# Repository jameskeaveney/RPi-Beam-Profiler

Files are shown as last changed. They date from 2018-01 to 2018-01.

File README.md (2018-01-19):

Raspberry Pi Beam Profiler
==========================
**Version 1.0.0**

A platform for inexpensive automatic laser beam profiling for finding the focal position and beam width of a laser beam, using a commercial translation stage, stepper motor, raspberry pi computer and the Pi NoIR camera module.

This repository contains the electronics schematics, mechanical drawings, list of components and python codes to construct and run the Raspberry Pi Beam Profiler.

See the user guide PDF for detailed installation instructions.

The paper, currently available on the arxiv (arxiv.org/abs/...), details the operation and exemplifies some results from the beam profiler.

-----------------

**Revision History**

v1.0.0
- Initial commit

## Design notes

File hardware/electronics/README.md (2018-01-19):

These are the electronic design files for the RPi beam profiler. 

The design files use KiCAD (http://kicad-pcb.org/). The PCB designs can be uploaded in their current .kicad_pcb file format to oshpark.com for board manufacture. If gerber files are required, open the pcb file in KiCAD first and output gerber files from there.

The daughter board sits on top of the RPi GPIO pins, and includes:

> A high-current 5V voltage regulator to power the RPi
> The Pololu DRV8825 motor controller breakout board

This should be powered by a high current (> 2A) DC voltage supplied via the barrel connector (centre positive).

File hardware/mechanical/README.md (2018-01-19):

Mechanical drawings for the Raspberry Pi Beam Profiler.

Drawings are provided as pdf files and Autodesk inventor (2016 version) IPT files.

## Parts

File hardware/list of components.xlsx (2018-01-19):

Raspberry Pi Beam Profiler - list of component parts
Off-the-shelf components - mechanical
Item | Quantity | Supplier | Part Number / Order Code | Web link
Translation Stage | 1 | Thorlabs | PT1/M | https://www.thorlabs.com/thorproduct.cfm?partnumber=PT1/M
Post holder | 2 | Thorlabs | PH20/M
Posts (or longer depending on need) | 2 | Thorlabs | TR50/M
16mm cage rods (longer or shorter depending on need) | 2 | Thorlabs | SR4
Thumb-screw | 1 | Thorlabs | TS6H/M
Stepper motor - Nanotec ST4209S1006-B | 1 | Farnell | 4743143 | http://uk.farnell.com/nanotec/st4209s1006-b/stepper-motor-0-9deg-2-phase/dp/4743143?ost=Nanotec+ST4209S1006-B&iscrfnonsku=false
Flexible shaft coupling - Ruland MWS20-5-5-SS | 1 | RS | 325-8218 | https://uk.rs-online.com/web/p/flexible-beam-couplings/3258218/
M2.5 standoffs (8mm, but length not important) | 8
M2 standoffs (5mm length) | 4 |  | 500-6558 | https://uk.rs-online.com/web/p/threaded-standoffs/5006558/
M2.5x6mm screws | 8
M3x6mm screws | 13
M6x12mm socket-head cap screw | 2
M2x3mm set screw | 2
M2x4mm screws | 4
M2x8mm screws | 2
Custom components - mechanical
Base plate | 1
Motor holder | 1
Micro-switch holder | 1
Camera mount | 1
Camera filter mount - SM1 adapter | 1
Symmetric post-mounting piece | 1
Custom screw | 1
Screw housing | 1
Electronics mount | 1
Off the shelf components - electronics
Raspberry Pi Model 3 B | 1 | RS | 896-8660 | https://uk.rs-online.com/web/p/processor-microcontroller-development-kits/8968660/
Raspberry Pi NOIR Camera | 1 | RS | 913-2673 | https://uk.rs-online.com/web/p/video-modules/9132673/
Pololu DRV8825 Breakout board | 1 | Hobbytronics | DRV8825 | http://www.hobbytronics.co.uk/drv8825-stepper-motor-driver
0.1" Jumper wires | 6 | Hobbytronics | PRT-12796 | http://www.hobbytronics.co.uk/cables-connectors/jumper-wires/jumper-wires-ff-6in
DC Barrel Jack Power supply, 12V, 3A | 1 | RS | 903-2902 | https://uk.rs-online.com/web/p/plug-in-power-supply/9032902/
Micro-switch, DM1-02P-30-3 | 1 | Farnell | SW05202 | http://onecall.farnell.com/multicomp/dm1-02p-30-3/microswitch-spdt-1a-sim-lever/dp/SW05202?ost=SW05202
Custom components -electronics
Power and motor controller board | 1

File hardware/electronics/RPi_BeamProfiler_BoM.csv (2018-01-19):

Id | Designator | Package | Quantity | Designation | Supplier and ref
1 | C1,C3 | CP_Radial_D6.3mm_P2.50mm | 2 | 100uF
2 | C2 | CP_Radial_D10.0mm_P5.00mm | 1 | 1000uF
3 | CON1 | BARREL_JACK | 1 | BARREL_JACK
4 | D1 | D_5W_P5.08mm_Vertical_AnodeUp | 1 | 1N5822
5 | L1 | INDUCTOR_V | 1 | 100 uH
6 | SW1 | Pin_Header_Straight_1x02_Pitch2.54mm | 1 | SW_DIP_x01
7 | SW2 | SW_DIP_x1_W7.62mm_Slide_LowProfile | 1 | SW_DIP_x01
8 | U1 | TO-220-5_Pentawatt_Multiwatt-5_Vertical_StaggeredType1 | 1 | LM2576HVS-5
9 | U3 | DRV8825_BreakoutBoard | 1 | DRV8825BreakoutBoard
10 | U2 | Pin_Header_Straight_2x20_Pitch2.54mm | 1 | Raspberry_Pi_2_3
11 | P1 | Pin_Header_Straight_1x04_Pitch2.54mm | 1 | CONN_01X04
Plus additional 0.1" headers for attaching connecting the DRV8825 breakout board (e.g. http://www.hobbytronics.co.uk/cables-connectors/pcb-headers-sockets/36way-header-254)

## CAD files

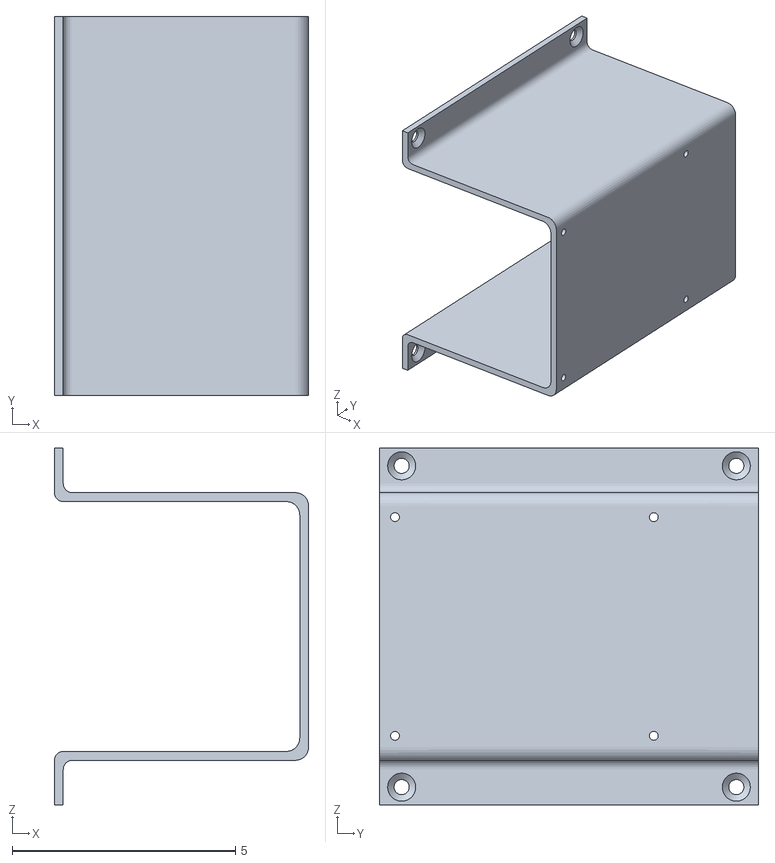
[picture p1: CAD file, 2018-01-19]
hardware/mechanical/drawings/electronics_mount_3dprint.stl
5.70 x 8.50 x 8.00

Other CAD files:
hardware/electronics/KiCAD files/RPi_BeamProfiler.kicad_pcb_Outline.ipt

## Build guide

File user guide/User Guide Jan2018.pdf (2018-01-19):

## Raspberry Pi Beam Profiler

## Users Guide

James Keaveney
james.keaveney@durham.ac.uk

Version 1.0.0

Last updated 2018/01/19

Contents

1. Introduction
2. Setting up the hardware
a. Stuff you will need
b. What goes where
3. Setting up the Raspberry Pi
4. Software Guide
a. Starting the software
b. The front panel
c. Live View
d. Camera settings
e. Translation stage scan settings
f. Export options
g. Image analysis method
h. Program Information
5. Hardware specifications

### 1. Introduction

The Raspberry Pi beam profiler is designed to be a replacement for knife-edging, particularly with one or two fixed-mount lenses where the focal point and size need to be known.

With a conventional knife-edging setup, this task is laborious and time-consuming. With this beam profiler, the idea is to completely automate the process.

It is also possible to perform M-squared measurements of beam quality or further analysis by outputting the raw image data.

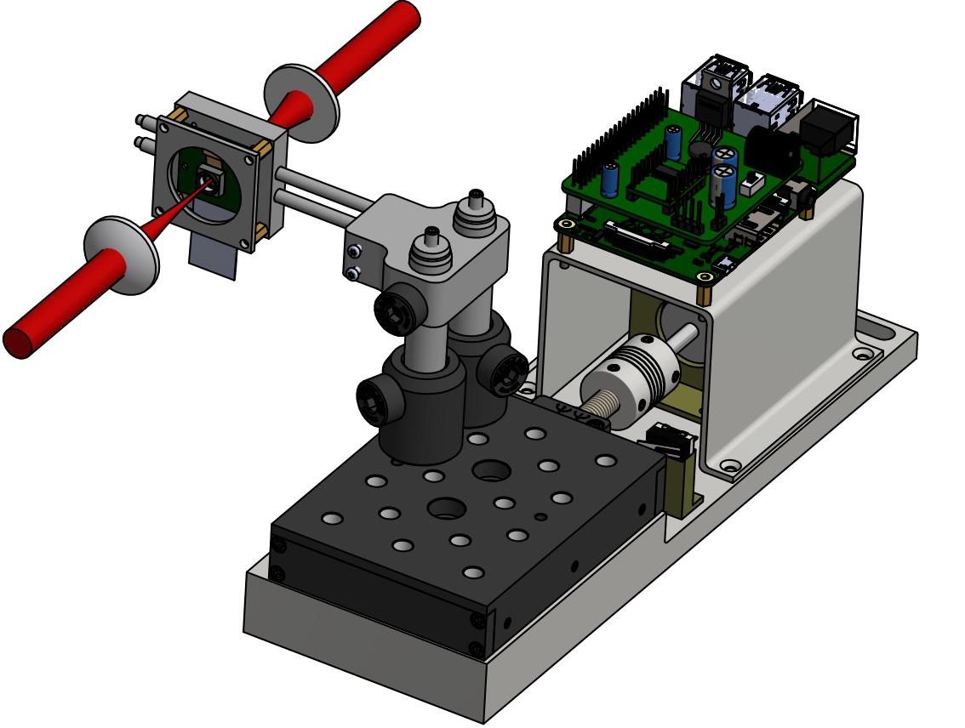
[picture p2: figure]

### 2. Setting up the hardware

a. What you will need:

In addition to the main beam profiler assembly, you will need the following parts:

- Raspberry Pi – we recommend the Model 3B version (or whichever is the latest), since it has by far the most processing power
- A micro-SD card with at least 8 GB capacity. We recommend getting a card with a fast read speed, which will maximise system performance.
- HDMI to HDMI / DVI cable, for connecting a monitor
- Monitor with either DVI or HDMI input. Recommended resolution of at least 1440 x 900.
- Keyboard and Mouse (both USB)
- USB memory stick for retrieving data
- DC power supply, with a barrel jack connector, capable of supplying 8-12 V with more than 2A to power the Raspberry Pi and stepper motor

The RPi’s local storage is a Micro-SD card. This should be installed, located near the bottom of the board, on the reverse side, as it stands in the beam profiler. We recommend using the Raspbian operating system (see section 3 below).

b. What goes where?

We recommend manufacturing the PCB designed for this purpose, in which case the PCB pushes on to the Raspberry Pi via the 2x20 GPIO header connection. However, it is not required, and the DRV8825 breakout board can be used by itself with only a few GPIO pin connections (note in this case the raspberry pi will have to be powered separately via the Micro-USB connector on the RPi board itself). For manually connecting the pins, the connection diagram is shown schematically below, along with the pin numbering scheme of the Raspberry Pi (Model B+, Model 2B, Model 3B).

CAUTION: Incorrect wiring could lead to short circuits which WILL damage the Raspberry Pi. Make sure it’s right before turning on, and never connect or disconnect anything while the Raspberry Pi is powered up.

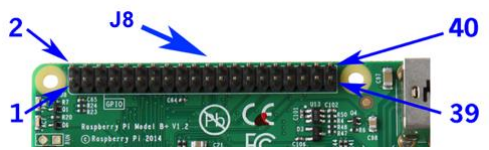
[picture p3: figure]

Figure 1: Raspberry Pi Model B+ GPIO Header pin numbering. The odd-numbered pins are along one side, and pin 2 is located nearest the edge of the RPi board. Image from http://pi4j.com/pins/model-b-plus.html

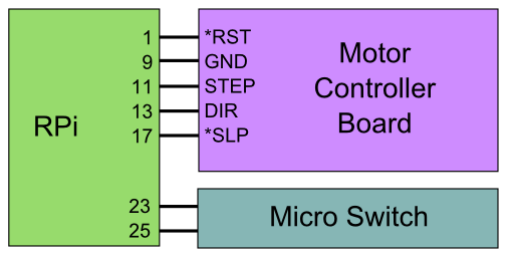
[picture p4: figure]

Figure 2: Connection diagram. Pin numbers on the RPi correspond to those in figure 1. The pins on the Motor controller are labelled accordingly.

Connect jumper wires between the pins of the RPi and Motor controller, as shown in figure 2. Connect the stepper motor via the A1,A2,B1,B2 pins of the motor controller board. Finally, connect the micro-switch to the RPi.

The motor controller is a Polou breakout board (product page here), (http://www.pololu.com/product/2133) consisting of a DRV8825 chip (datasheet is here). (http://www.pololu.com/file/download/drv8825.pdf?file_id=0J590) This is capable of driving up to 2.2A per coil. The current is actively controlled, and a potentiometer controls the current limit. If a different stepper motor is used, this current limit can be reset for the new motor (follow the instructions on the Polou website).

Mounting the CCD

The CCD assembly should be placed in the holder with the ribbon cable pointing down. This is not a necessity, but the images displayed on the software will be rotated 180 degrees. The CCD can face either direction in the translation (z-) axis, in case multiple beams need to be profiled that travel in different directions, for example a counter-propagating setup for 2-photon EIT.

A combination of any of Thorlabs’ standard ½” posts (part # TRxxx/M) and 16 mm cage rods (part # SRx) can be used to set the x- and y-position of the camera mount.

### 3. Setting up the Raspberry Pi

a. Installing Raspbian

The operating system we recommend is called Raspbian, a version of Debian Linux. These instructions assume this operating system is used.

Download the latest version of Raspbian from https://www.raspberrypi.org/downloads/raspbian/

Install the operating system to the SD card following the installation guide at https://www.raspberrypi.org/documentation/installation/installing-images/

Once all other cables are connected, plug in the power cable. There is no On/Off switch on the RPi, so it should start immediately. There are some indicator lights that should light up as soon as you power-up.

The device should boot to a desktop environment. The operating system is a variant on debian, a linux distribution. If you are not familiar with this type of operating system, google it!

b. Installation of python modules:

After Raspbian is installed, you will need to install some additional python modules which are required to run the beam profiler.

These can be installed via a terminal window through

sudo apt-get install <module1> <module2> ...

The modules that are needed are

python-matplotlib
python-scipy
python-wxgtk3.0

You should also make sure that the following modules are up-to-date:

python-numpy
python-picamera
python-rpi.gpio

All installed modules can be updated by doing the following:

sudo apt-get update
sudo apt-get upgrade
c. Enable the camera module

The camera module is not enabled by default. To enable it, open a terminal and type

sudo raspi-config

Go to Interfacing Options -> Camera -> Enable Camera. Move down to ‘Finish’ and reboot the Raspberry Pi.

d. Disable red LED on camera module

To avoid additional noise on the camera, you should disable the red LED. To do this, edit the /boot/config.txt file, using

sudo nano /boot/config.txt

and add the line

disable_camera_led=1

to the end of the file. Save and exit (Ctrl+X, then follow instructions), then reboot the Raspberry pi (sudo reboot).

e. Installation of beam profiler software

Download the GitHub repository, either by navigating to the GitHub repository (https://github.com/jameskeaveney/RPi-Beam-Profiler) and downloading the zip file or by using the git command line tool (git should be installed already, but if not then ‘sudo apt-get install git’ in a terminal window). Running

git clone http://github.com/jameskeaveney/RPi-Beam-Profiler

will download the repository to the current directory.

Navigate to the \software\RPiBeamProfilerApp sub-directory, and type

sudo python beamprofiler_guiX.Y.py

where X.Y is the version number.

### 4. Software Guide

On starting the software, the program will try to calibrate the translation stage. The stage is moved backwards (towards the motor) until the microswitch is triggered. This stops the stage moving and is used as the 0.00 mm reference point. The user is presented with a dialog box to confirm this is happening. When the dialog box disappears the program is ready to continue.

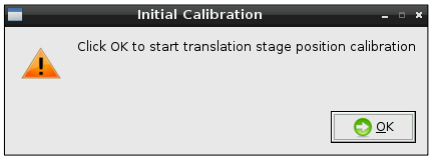
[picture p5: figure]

Initial calibration dialog

a. The front panel

The front panel of the program is shown below. On the left side of the screen, the current image is shown, along with the x-axis and y-axis slices (the 2d image array is integrated along one axis to give the slice in the other axis). The y-axis is the vertical axis (direction of the ribbon cable).

Bottom left are the fitted beam waists in x- (top) and y-axes (bottom), as a function of translation stage position (z-axis). This will dynamically update when a translation stage scan is run.

This is a plot using matplotlib, and as such is interactive – any axis can be panned or zoomed using the controls on the toolbar at the bottom left of the screen.

On the right side of the front panel are the various controls, which will be detailed separately below.

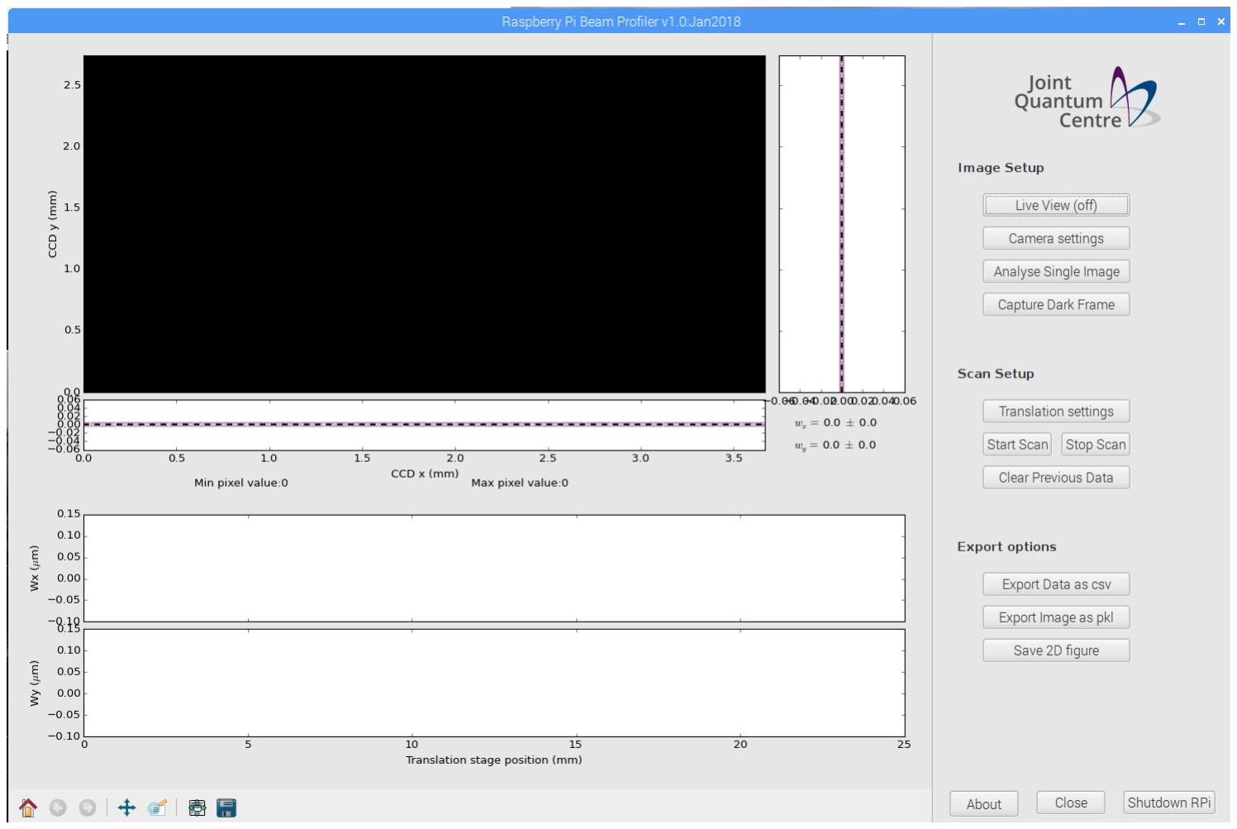
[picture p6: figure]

The front panel, as it appears on starting the program.

b. Live View

The first button is called LiveView, and is intended as an alignment aid. It brings up a video feed of the ccd image. Because of the way this preview works, this is a full-color image so may look a bit weird! This is fed through with the default amount of post-processing (there is no option to disable this), so is not representative of the still image quality. The video is also cropped to the central area of the ccd, and is in 16:9 format.

Just to stress the point – the live view is not indicative of the image quality of the still images – these will be much better!

c. Camera settings

The camera settings sub-menu contains the controls for setting exposure time and area-of-interest. The interface is shown below.

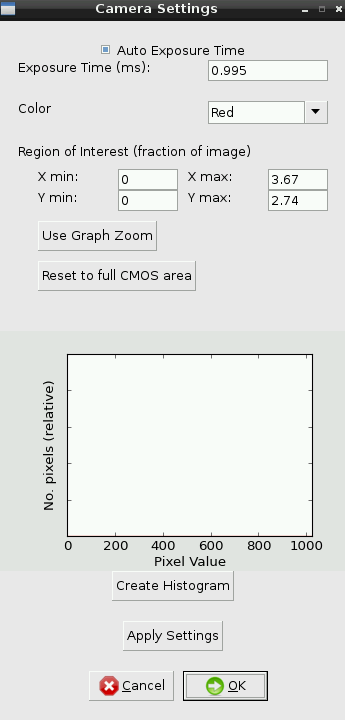
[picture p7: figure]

Camera settings sub-menu.

The exposure time is controlled either automatically, when the tick-box is selected, or manually through the text entry box (values in milliseconds). The minimum exposure time is 9 or 12 µs (version 1 or 2 sensor), maximum is a few seconds. Auto-exposure works by analysing an image frame and making sure that no pixels are saturated, which is fundamentally different from how normal camera auto-exposure metering works.

The next control is for the color of pixel used. Since the physical sensor has filtered pixels arranged in a Bayer pattern (see section 4), we must select which set of pixels to use, since they have different sensitivity depending on wavelength.

The final control is the region-of-interest (ROI), which essentially crops the image in to a specific area. This makes fitting faster, since there is less data to process, so is recommended for use with small beams.

There are two ways to set these parameters – either by using the text input boxes, or by zooming the graph using the matplotlib toolbar buttons (discussed above). This must be done with the sub-menu closed, so zoom in, open the sub-menu, and then click on ‘Use Graph Zoom’, which will then update the text boxes with the current axis limits. To go back to the full sensor area, click the ‘Reset to...’ button.

Clicking ‘Apply Settings’ will save the current exposure / ROI settings and take an image, without closing the menu.

NOTE: None of these parameters are saved until the ‘Apply’ button is pressed. Closing the window without pressing apply will NOT save any changes.

Finally, there is also the option to look at a histogram of the current image, which may be useful for a quick look at the distribution of pixel values (e.g. checking for saturation when in manual exposure mode)

d. Translation stage scan settings

The translation scan settings sub-menu controls the position of the translation stage, the start/stop positions of a scan and the step size. The sub-menu interface is shown below.

The translation stage is designed to move a maximum of 25 mm, however the stage becomes difficult to move near the edge of it’s movement range so this is limited (in software) to 0 - 23 mm. The step size can be very small, down to 1 micron, however this may not be enough to overcome static friction so results may be variable!

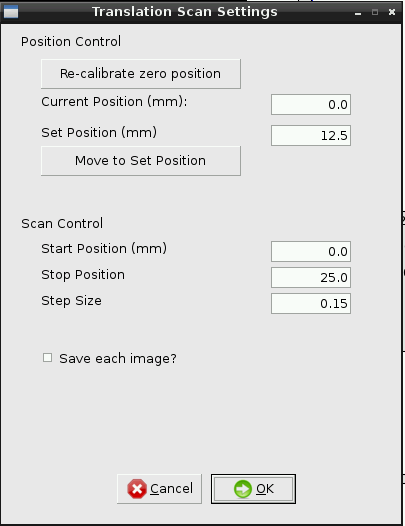
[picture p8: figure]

Translation settings sub-menu.

There is the option to re-calibrate the zero position, which re-runs the routine that happens on starting the program (see above for details). The current position text box is read-only, and displays (strangely enough) the position relative to the zero of the translation stage. The set position box and button allows movement to a specific position.

The scan control inputs control the starting and final positions of the stage, and the step size.

The ‘save each image’ tick box will automatically save an image at each position of the translation stage. When the start scan button is pressed and this option is selected, the user will be prompted to select a location and filename for the images. A number is appended to the filename for each image, with 0 corresponding to the start of the translation scan. They are saved as pickled (binary) data files – see the section on exporting data for more information.

WARNING: If multiple scans are run, the ‘save each image’ option will overwrite existing files with the same name.

Running a scan

To run a scan, click the ‘Start Scan’ button on the front panel. The stage will move to the start position, capture an image and fit x- and y-axis waists. To cancel the scan running, click the ‘Stop Scan’ button. Be aware it may take a little while to respond if an image acquisition / analysis is in progress.

By default the data does not clear between scans, the idea being that the first scan would be fairly coarsely spaced to find the rough focus position and then a finer scan would be performed around the focal point. In this case all the data is still useful, so the plot does not clear. If the data is not wanted, click the ‘Clear previous data’ button to start with a blank canvas.

e. Export options

The final 3 buttons on the main panel are for exporting data. Data can be saved direct to the RPi’s SD card, but space is fairly limited so a better alternative is to use a USB flash drive.

‘Export data as csv’ exports the two curves of beam waist against position, in order of increasing position coordinate. The output is in csv (comma separated value) format and is therefore readable by spreadsheet programs as well as Python etc. The data is arranged in columns as follows:

z-position (mm), x-waist (μm), x-error (μm), y-waist (μm), y-error (μm)

The ‘Export image as pkl’ button exports the current image as a python pickle file, which is a binary output format for quickly reading in to python again. Saving the image as a 2D csv file is computationally expensive for such a little computer… (the file sizes are ~4 MB, which takes over a minute to write). If csv files are required, they can be written using a separate python script called pkl_to_csv.py located in the /beamprofiler directory

The script pkl_to_image.py reads in a particular image and produces a matplotlib plot similar to the one in the beamprofiler app. The plot is automatically saved in both png and pdf format. Run this from the command line specifying the file to be read. For example,

python pkl_to_image.py imagefile.pkl

will read in the file imagefile.pkl and produce two new files, imagefile.png and imagefile.pdf.

The pickled image files can be read into another python script using the following:

import cPickle as pickle
IMG = pickle.load(open(<FILENAME>,’rb’))

where IMG is a numpy 2d-array and <FILENAME> is the filename (including path location if necessary) of the .pkl file.

Finally, ‘Save 2D figure’ saves the left-hand side of the front panel (everything apart from the button bar) in the same way as matplotlib saves figures. This has the same function as the save icon on the matplotlib toolbar.

### 5. Image analysis methods

The images are fitted to 1D Gaussian functions of the form

I(x) = A exp(−

2(x − c)

2
w²

)

Where x is the horizontal or vertical coordinate, and w is the 1/e² radius.

After the translation stage scan, the profile is fit to a function of the form

wx,y

(z) = w0 √1 + (
(z − zc

)
zR

)

2

Fitting is done via the curve_fit method which is part of scipy.optimize. Errors in all fit parameters are found from the covariance matrix (square-root of the diagonal elements).

f. Program information

The program is written entirely in Python, and uses the following modules:

wxpython – GUI

matplotlib – plotting

numpy, scipy – numeric, arrays, fitting routines

RPi.GPIO – raspberry pi specific module for interfacing with the GPIO (general purpose input/output) pins

picamera – raspberry pi specific module for interfacing with the camera

The program is entirely open-source. It is therefore possible (and encouraged!) to add further functionality to the software yourself. Should you do so, please fork the GitHub repository to make your improvements publicly available.

6. Hardware specifications

The camera is the PiNOIR camera, which is a normal CMOS camera, but crucially without an infra-red filter, which allows us to use the full wavelength sensitivity range of the silicon sensor – should be roughly 300 – 1100 nm (not tested!). It’s therefore bounded by the usual limits of silicon, and is more sensitive in the region of around 750 nm.

A. Camera specifications:

Sensor area: 3.67 x 2.54 mm
Total number of pixels: 2592 x 1944 (v1), 3280 x 2464 (v2) Pixel pitch: 1.4 µm (v1), 1.12 µm (v2)

Bayer pattern:

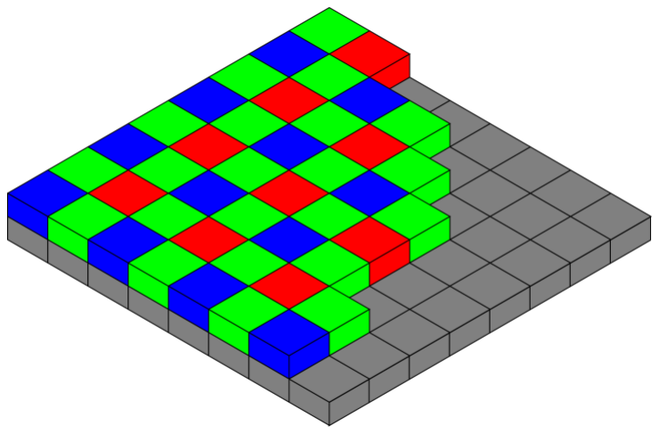
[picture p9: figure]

Bayer Pattern. Image from Wikipedia.

Like all colour sensors, the raw data only has ¼ the number of total pixels for red and blue, and ½ the number of total pixels for green. Since we want the raw data, we have two options – either interpolate back to the full resolution of the camera, or use just the R, G or B pixels and lose a factor of 2 in resolution.

b. Translation Stage Specifications

The translation stage is a Thorlabs PT1/M, (http://www.thorlabs.de/newgrouppage9.cfm?objectgroup_id=706) with a custom 0.5 mm pitch screw thread. This means that one revolution moves the stage by 500 µm. The stepper motor (datasheet here, (http://www.farnell.com/datasheets/1375212.pdf) model number ST4209S1006-B) has a single step resolution of 0.9 degrees, so in theory the system has a spatial step size of 500 x 0.9 / 360 = 1.25 µm.

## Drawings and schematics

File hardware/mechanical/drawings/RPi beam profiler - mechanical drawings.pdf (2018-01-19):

# Raspberry Pi Beam Profiler

## Mechanical drawings

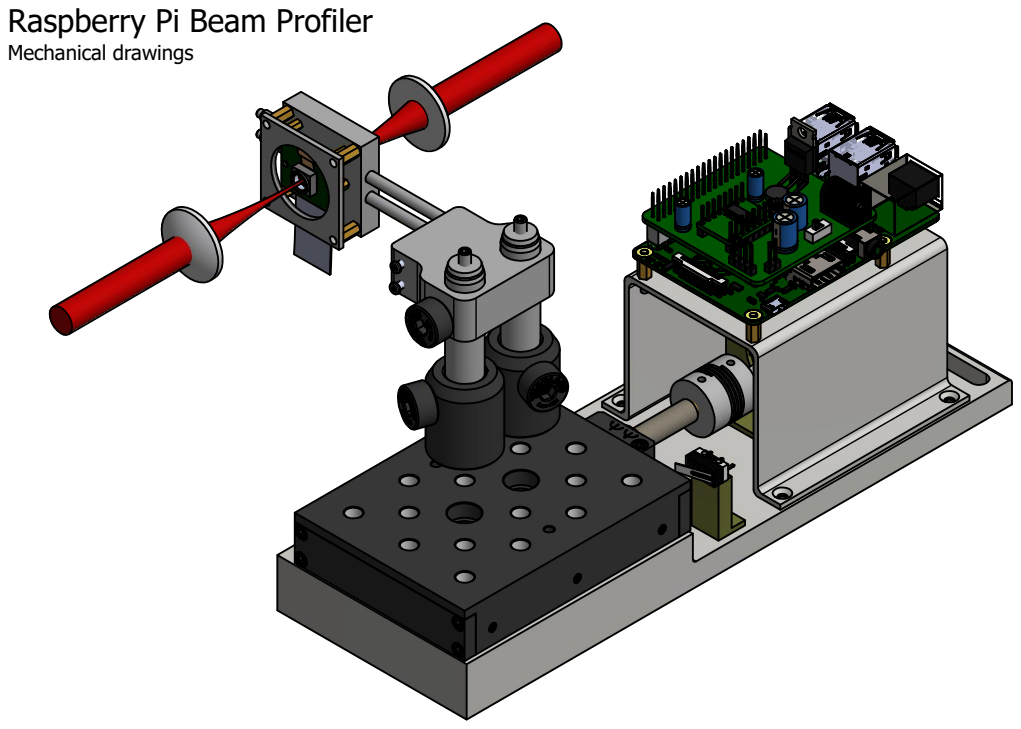
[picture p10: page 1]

# Reversible sensor orientation

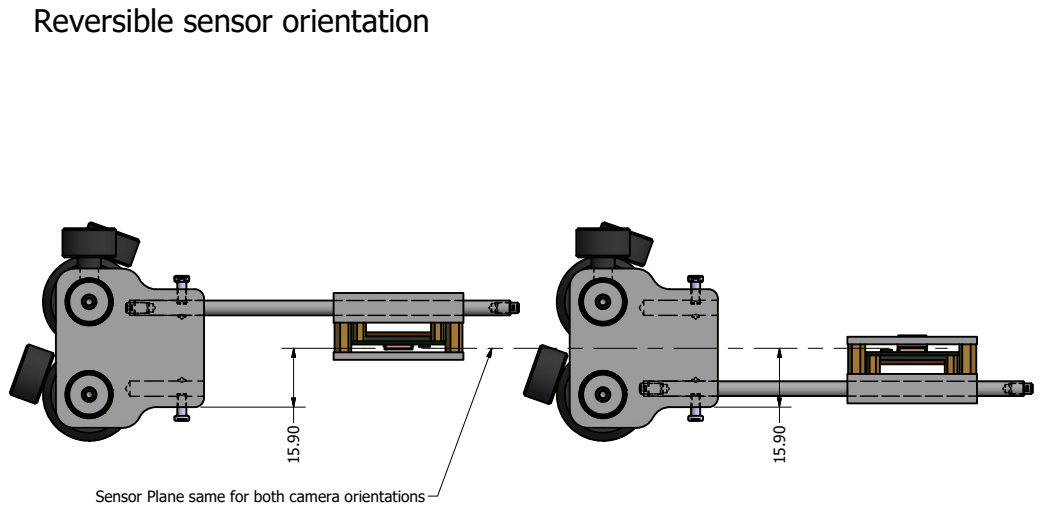
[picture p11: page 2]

Sensor Plane same for both camera orientations

# Individual Components

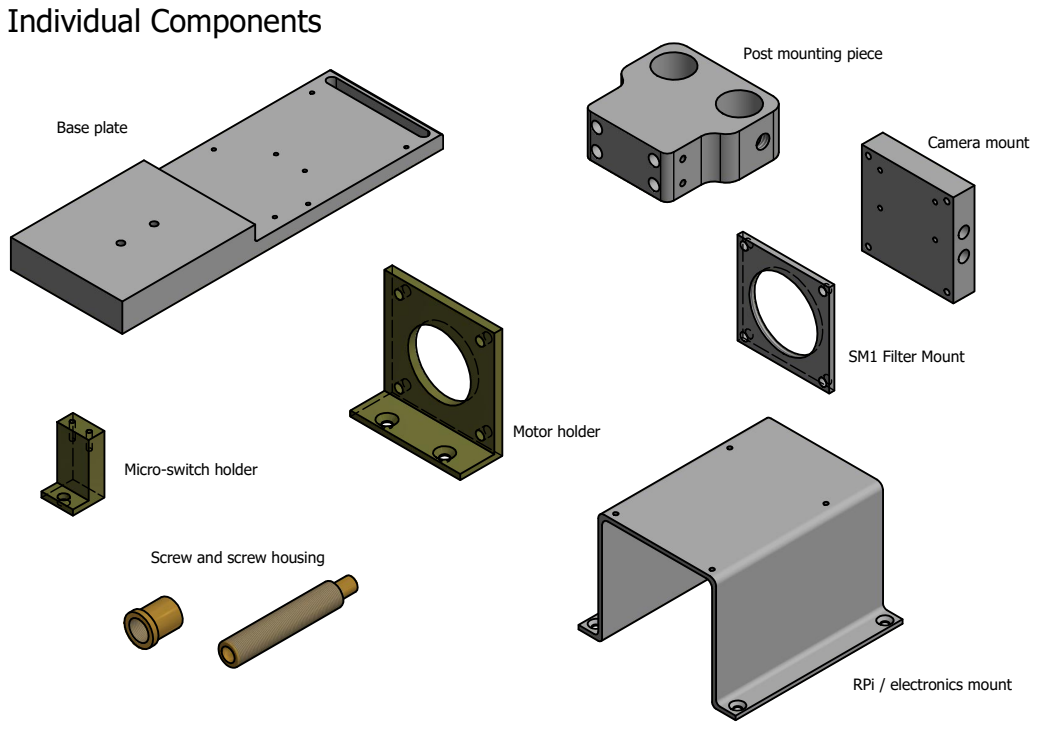
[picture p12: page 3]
Camera mount; SM1 Filter Mount; Motor holder; Base plate

Post mounting piece

Micro-switch holder

Screw and screw housing

RPi / electronics mount

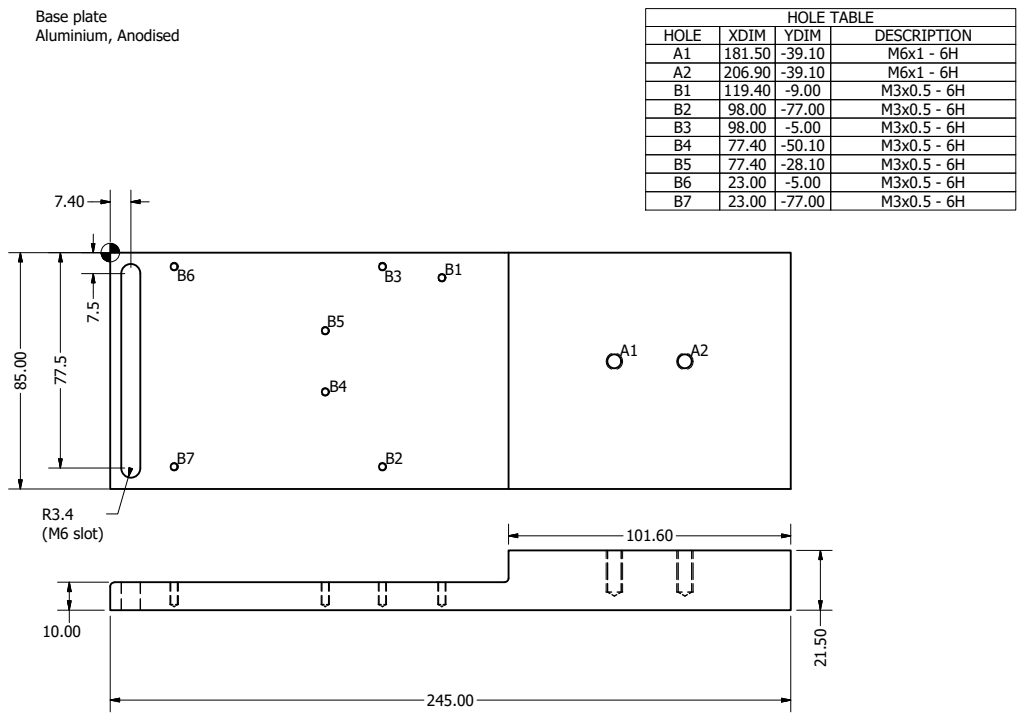
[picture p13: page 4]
R3.4 (M6 slot); Base plate Aluminium, Anodised; HOLE TABLE; HOLE; XDIM; YDIM; DESCRIPTION

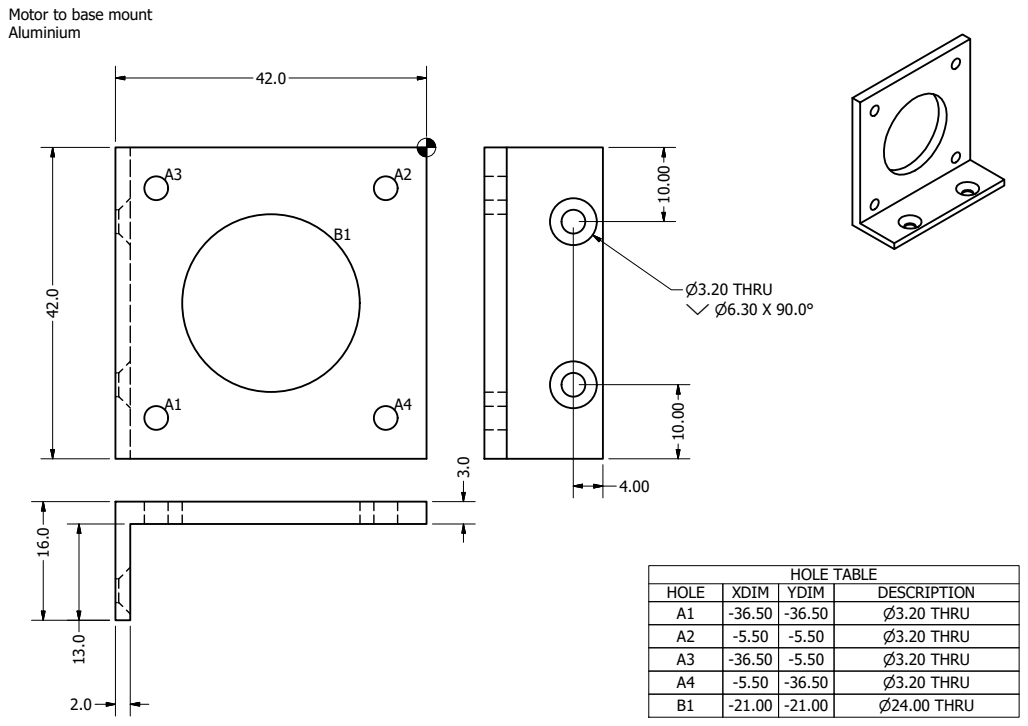
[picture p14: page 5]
HOLE TABLE; HOLE; XDIM YDIM; DESCRIPTION; P3.20 THRU; P24.00 THRU; P3.20 THRU Y P6.30 X 90.0°

Motor to base mount
Aluminium

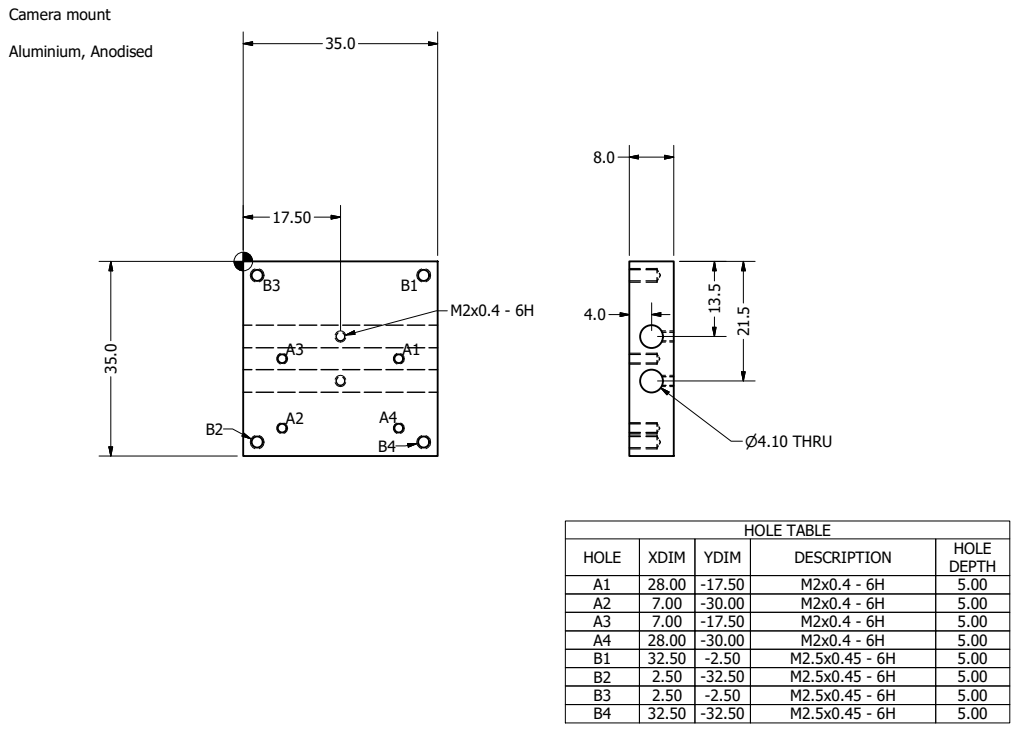
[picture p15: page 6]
P4.10 THRU; HOLE TABLE; HOLE; XDIM; YDIM; DESCRIPTION; HOLE DEPTH; Camera mount; Aluminium, Anodised

Camera filter mount - SM1 adapter

Material - Aluminium, Anodised

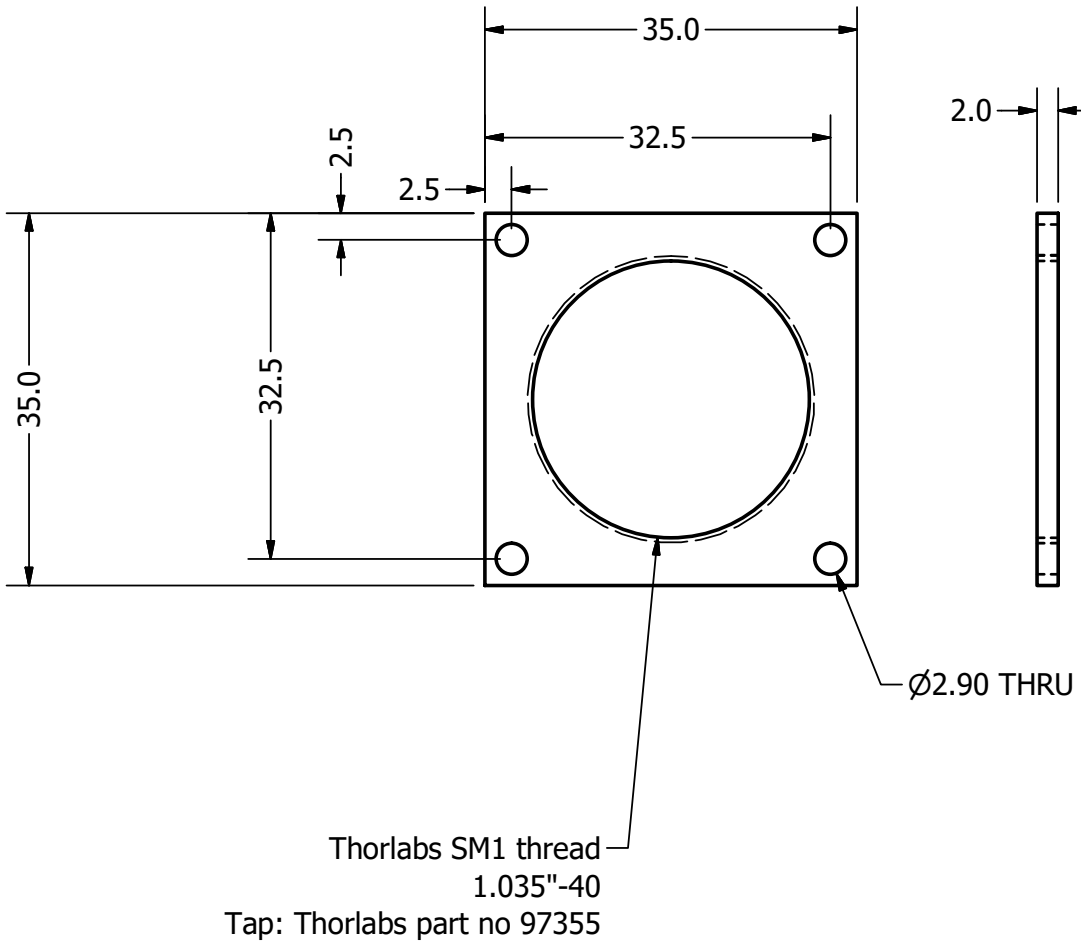
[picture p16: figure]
Thorlabs SM1 thread 1.035"-40 Tap: Thorlabs part no 97355; P2.90 THRU

Micro-switch holder

Material: Any metal

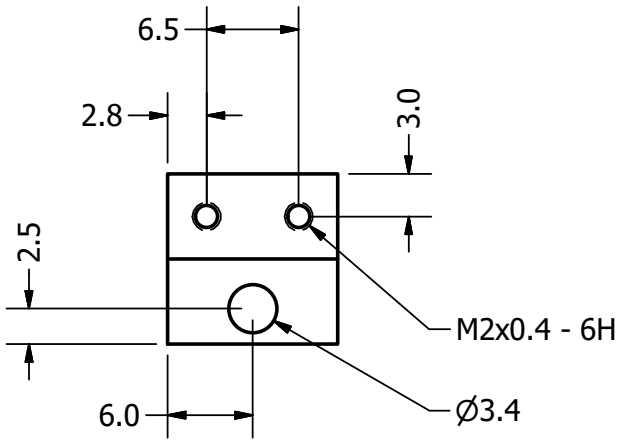
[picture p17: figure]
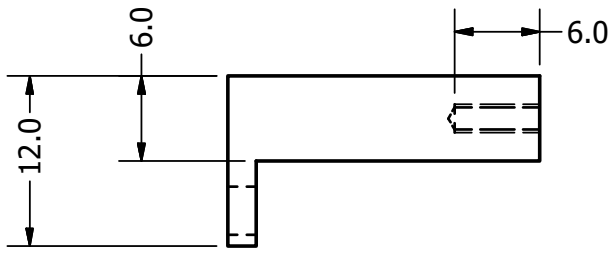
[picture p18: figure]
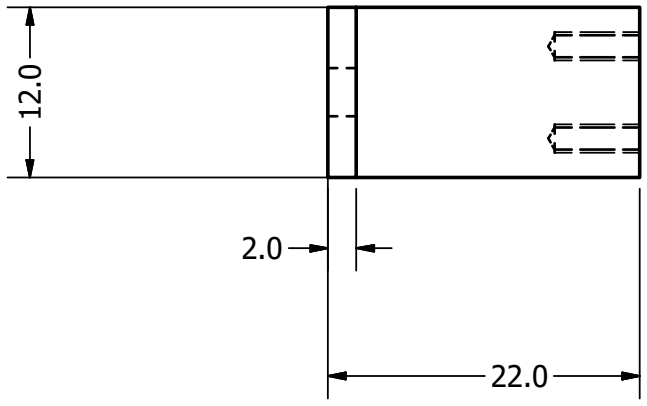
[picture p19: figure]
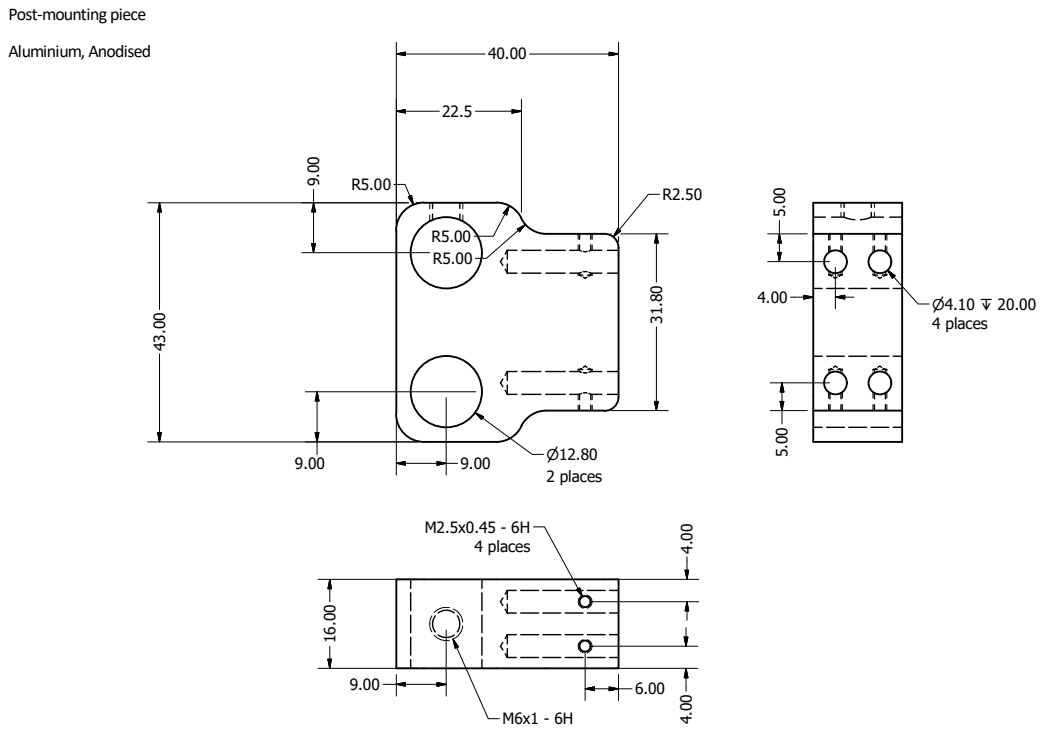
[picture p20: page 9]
2 places; 4 places; M2.5x0.45 - 6H 4 places; Aluminium, Anodised

Post-mounting piece

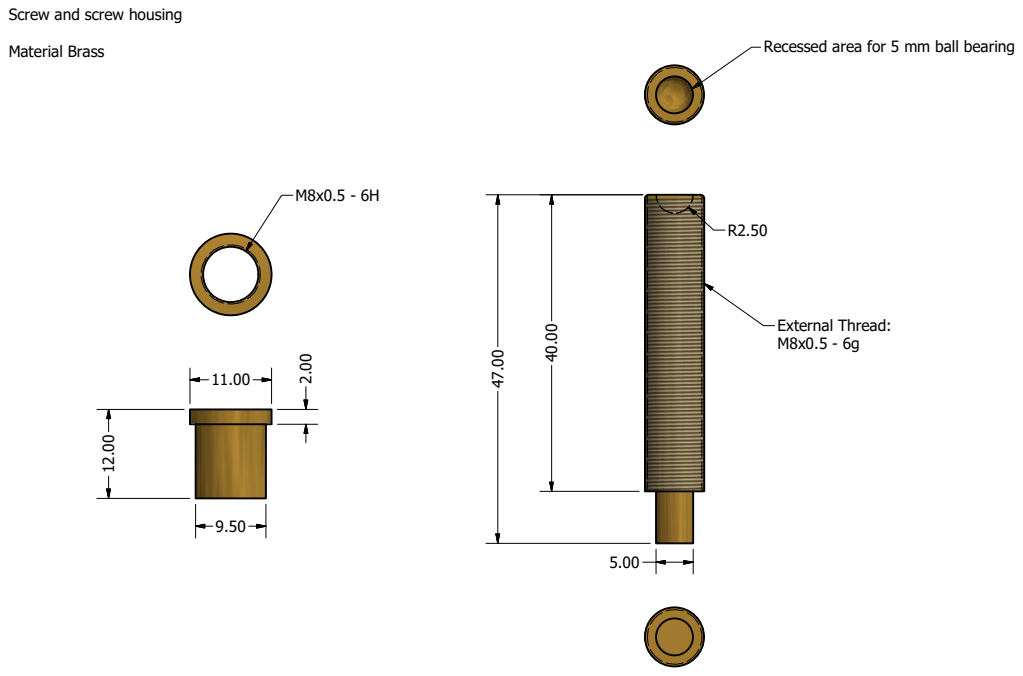
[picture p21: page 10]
External Thread:; Material Brass

Screw and screw housing

Recessed area for 5 mm ball bearing

Ele; ble; ile



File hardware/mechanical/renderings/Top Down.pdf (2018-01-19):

# Top-down view

dju; sta; ble; dista; xis

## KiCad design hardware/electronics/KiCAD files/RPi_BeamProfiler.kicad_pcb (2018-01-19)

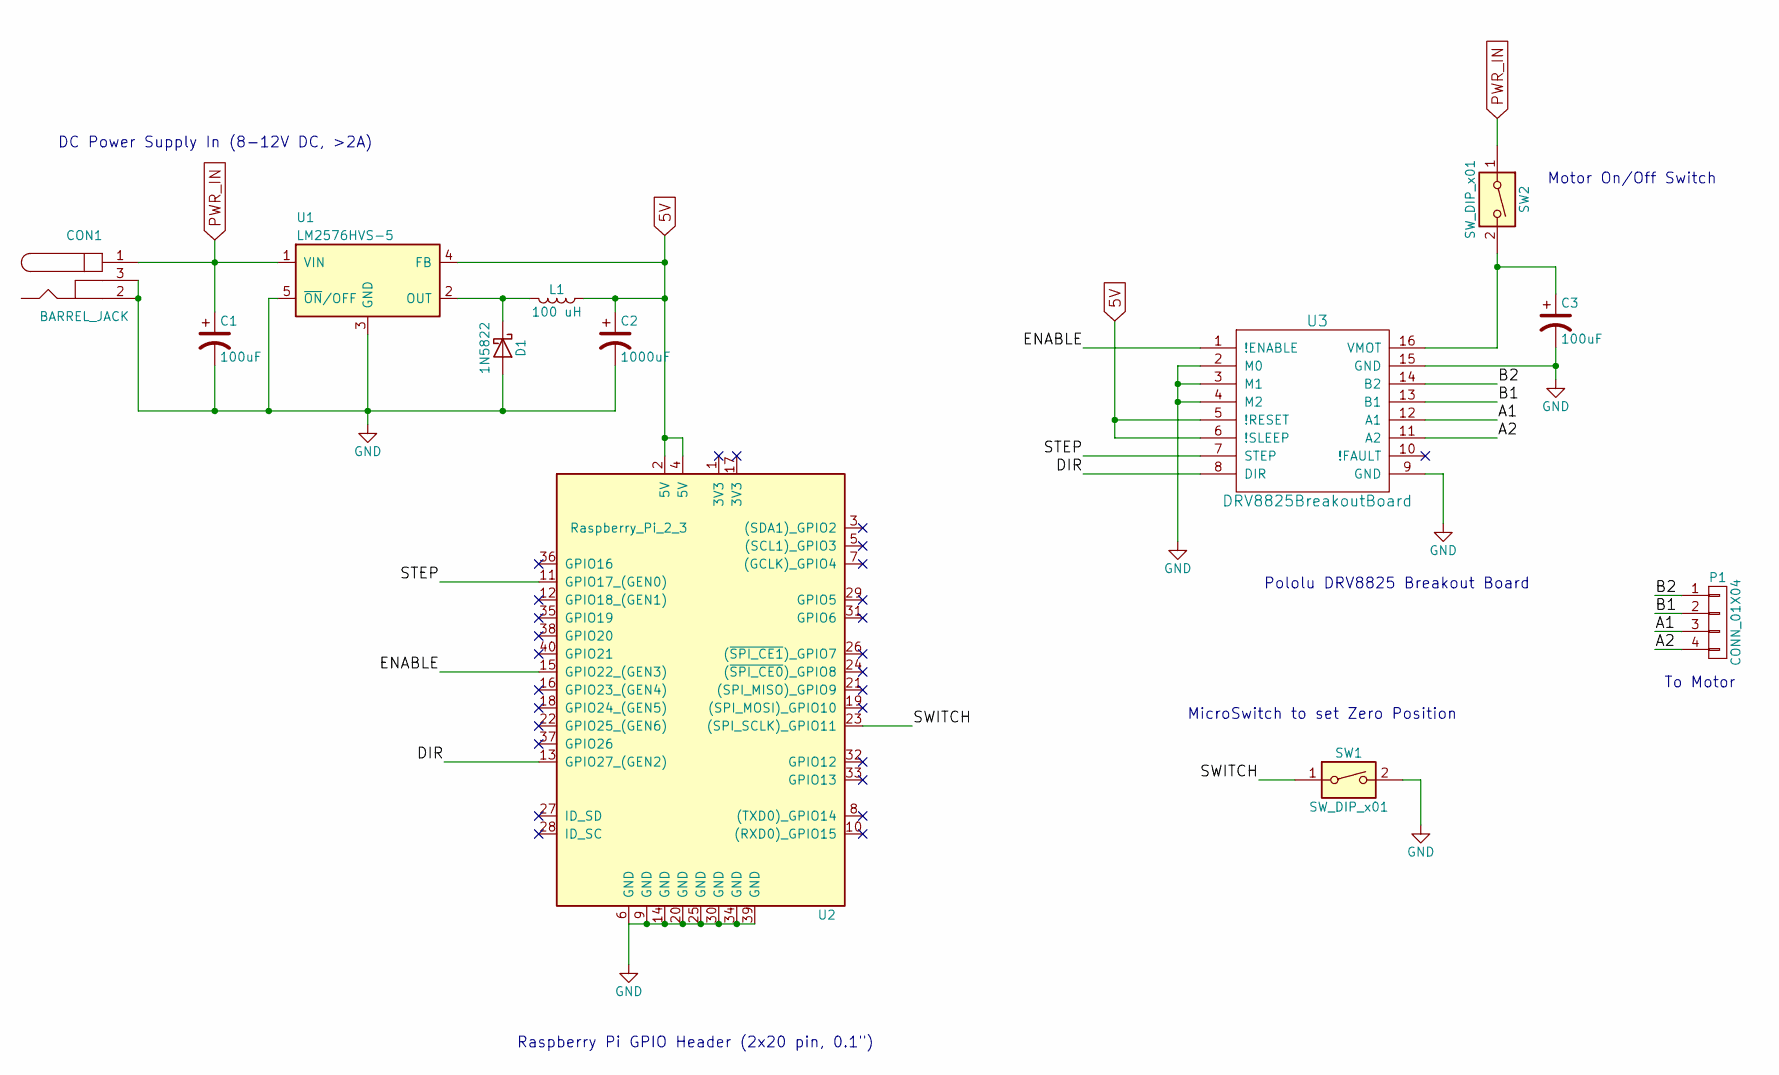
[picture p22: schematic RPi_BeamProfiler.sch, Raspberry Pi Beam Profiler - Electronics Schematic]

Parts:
C1, C3: 100uF; CP_Radial_D6.3mm_P2.50mm
C2: 1000uF; CP_Radial_D10.0mm_P5.00mm
CON1: BARREL_JACK
D1: 1N5822; D_5W_P5.08mm_Vertical_AnodeUp
L1: 100 uH; INDUCTOR_V
P1: CONN_01X04; Pin_Header_Straight_1x04_Pitch2.54mm
SW1: SW_DIP_x01; Pin_Header_Straight_1x02_Pitch2.54mm
SW2: SW_DIP_x01; SW_DIP_x1_W7.62mm_Slide_LowProfile
U1: LM2576HVS-5; TO-220-5_Pentawatt_Multiwatt-5_Vertical_StaggeredType1
U2: Raspberry_Pi_2_3; Pin_Header_Straight_2x20_Pitch2.54mm
U3: DRV8825BreakoutBoard; DRV8825_BreakoutBoard

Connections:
5V: C2.1, L1.1, U1.4 (FB), U2.2 (5V), U2.4 (5V), U3.5 (!RESET), U3.6 (!SLEEP)
/A1: P1.3, U3.12 (A1)
/A2: P1.4, U3.11 (A2)
/B1: P1.2, U3.13 (B1)
/B2: P1.1, U3.14 (B2)
/DIR: U2.13 (GPIO27_(GEN2)), U3.8 (DIR)
/ENABLE: U2.15 (GPIO22_(GEN3)), U3.1 (!ENABLE)
/STEP: U2.11 (GPIO17_(GEN0)), U3.7 (STEP)
/SWITCH: SW1.1, U2.23 ((SPI_SCLK)_GPIO11)
GND: C1.2, C2.2, C3.2, CON1.2, CON1.3, D1.2 (A), SW1.2, U1.3 (GND), U1.5 (~ON~/OFF), U2.6 (GND), U2.9 (GND), U2.14 (GND), U2.20 (GND), U2.25 (GND), U2.30 (GND), U2.34 (GND), U2.39 (GND), U3.2 (M0), U3.3 (M1), U3.4 (M2), U3.9 (GND), U3.15 (GND)
unnamed: C3.1, SW2.2, U3.16 (VMOT)
unnamed: D1.1 (K), L1.2, U1.2 (OUT)
PWR_IN: C1.1, CON1.1, SW2.1, U1.1 (VIN)

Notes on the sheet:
DC Power Supply In (8-12V DC, >2A)
Raspberry Pi GPIO Header (2x20 pin, 0.1")
Pololu DRV8825 Breakout Board
MicroSwitch to set Zero Position
Motor On/Off Switch
To Motor

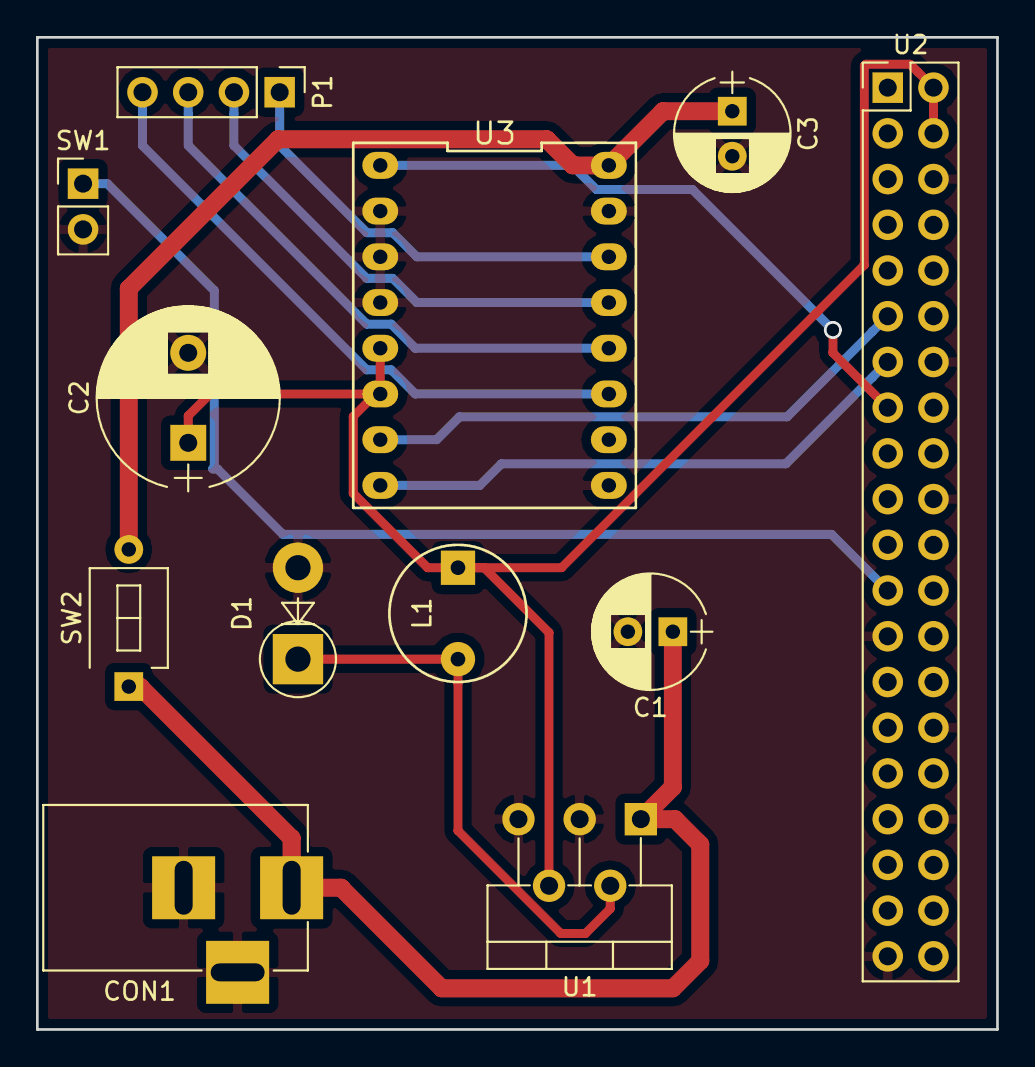
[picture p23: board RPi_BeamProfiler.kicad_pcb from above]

Board: 2 copper layers, 53.3 x 55.1 mm, 12 parts (0 on the bottom side), 13 nets.
